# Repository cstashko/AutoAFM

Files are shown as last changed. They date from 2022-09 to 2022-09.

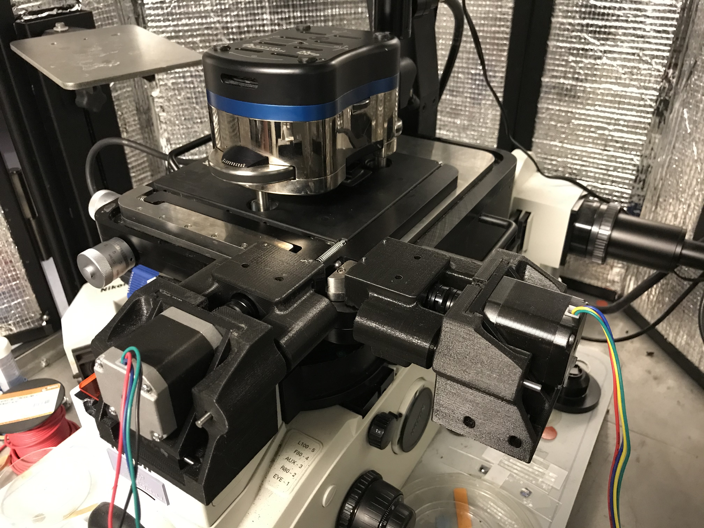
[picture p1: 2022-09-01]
AFM_pics/IMG-1473.jpg

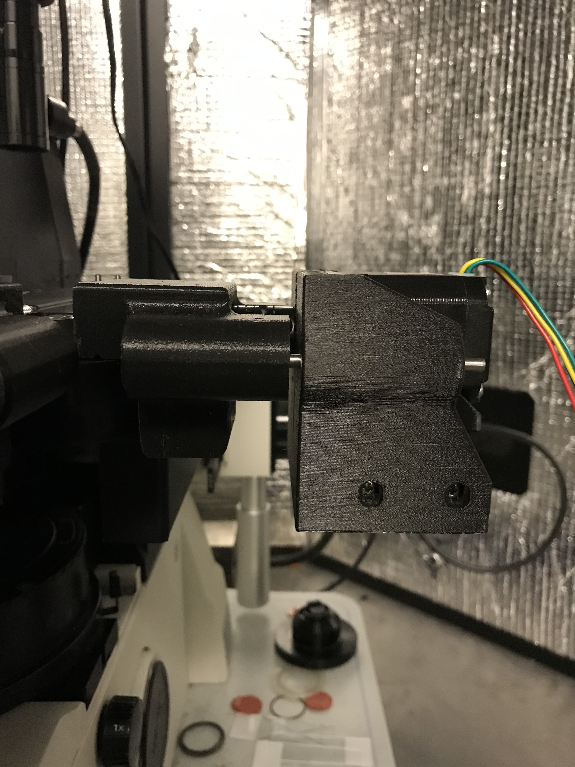
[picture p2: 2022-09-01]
AFM_pics/IMG-1471.jpg

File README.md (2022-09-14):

AutoAFM components, bill of materials, assembled view, and pictures

See STIFMap methods section for in-depth explanation of AutoAFM principles

Contact Connor Stashko (cstashko@berkeley.edu) for questions

AutoAFM Pipeline:  

    1. Thaw slide on hand and wash away OCT in PBS for 5 min  
    2. Probe PA gels of known stiffness as a baseline  
    3. Load tissue sample with approx. 250 uL of PBS + propidium iodide + CNA35   
    4. Open ‘STIFMap_Jupyter_script.ipynb’ in Jupyter and run it all  
    5. Open MicroManager  
        a. Load macros from 'STIFMap_micromanager_macros.txt'  
        b. Manually center AFM stage (in x and y axes)   
        c. Run ‘main’ in micromanager  
            i. Initializes the folders, but don’t do anything else in micromanager yet  
    6. Asylum things: Hook up motors, load ‘STIFMap_IGOR_Asylum_macros.txt’  
        a. Power motors with 12 V  
        b. 'Compile', 'connect', 'initialize', 'initialize'  
        c. Setup WatchFolder (‘WatchFolderPanel()’)  
            i. ‘In’ and ‘out’ in ‘AFM_expt_temp’  
        d. Change save directory to ‘out’ and uncheck ‘save to mem’  
        e. Change trigger to 1.8 nN  
        f. Set the force dist to ‘inf’ and ensure the velocity is 2 um/s  
    7. Move to the region of interest on the slide  
        a. Line up the stage with the optimal position  
        b. Follow the onscreen windows on MicroManager for ‘main’    
    8. Close door to AFM  
    9. At the end, check the position of the tip under BF to ensure it hasn’t changed much  
    10. Probe PA gels again to ensure tip elasticity did not drift during sample probing  
  
Known Issues:  
    • ImageJ won’t move folders/directories if they’re open in file viewer  
    • WatchFolderPanel can’t assign directories that don’t exist, so ‘main’ has to be run before setting input/output dirs  
    • Need a way to quit more elegantly if forcepoints don't trigger in Asylum

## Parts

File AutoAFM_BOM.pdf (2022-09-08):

ITEM NO. | DESCRIPTION | PROCESS | SUPPLIER | MATERIAL | PART NUMBER | QTY. | Package Qty | Unit Price ($) | Order Qty
1 | Microscope Stage_base | AFM Stage Base | INCLUDED | | | 1
2 | Microscope Stage_X | AFM Stage X Translation | INCLUDED | | | 1
3 | Microscope Stage_Y | AFM Stage Y Transation | INCLUDED | | | 1
4 | | AFM X Knob | INCLUDED | | | 1
5 | | AFM Y Knob | INCLUDED | | | 1
6 | | | PURCHASED | MCMASTER | 91290A190 | 4 | 10 | 7.11 | 1 | 7.11
7 | clamp_nut_90576A103 | | PURCHASED | MCMASTER | 90576A103 | 4 | 100 | 4.27 | 1 | 4.27
8 | | | PURCHASED | MCMASTER | 93475A230 | 4 | 100 | 1.86 | 1 | 1.86
9 | X_frame_main | Stage Frame_x | 3D PRINTED | | | 1
10 | NEMA 17 | Motor | INCLUDED | | NEMA 17 | 2
11 | motor_faceplate | Motor Bracket | 3D PRINTED | | | 2
12 | slider | Motor Frame | 3D PRINTED | | | 2
13 | wedge_1 | Bracket Adjuster_front | 3D PRINTED | | | 2
14 | wedge_2 | Bracket Adjuster_back | 3D PRINTED | | | 2
15 | | | PURCHASED | MCMASTER | 9044K113 | 4 | 3 | 5.26 | 2 | 10.52
16 | | Tensioning Pin | PURCHASED | MCMASTER | 91595A140 | 4 | 25 | 9.91 | 1 | 9.91
17 | | Bracket Adjusting Screws | PURCHASED | MCMASTER | 92000A077 | 4 | 50 | 9.94 | 1 | 9.94
18 | wedge_nut_90591A250 | | PURCHASED | MCMASTER | 90591A250 | 4 | 100 | 2.33 | 1 | 2.33
19 | | | PURCHASED | MCMASTER | 97310A111 | 4 | 100 | 2.86 | 1 | 2.86
20 | slider_pin_91585A389 | Alignment Rod | PURCHASED | MCMASTER | 91585A389 | 4 | 1 | 4.14 | 4 | 16.56
21 | motor_screw_91290A111 | Screws Motor into Motor Bracket | PURCHASED | MCMASTER | 91290A111 | 4 | 100 | 8.71 | 1 | 8.71
22 | X_frame_clamp | | 3D PRINTED | | | 1
23 | knob_cap | Knob Adapter | 3D PRINTED | | | 2
24 | knob_screw_90044A247 | Adapter Screw | PURCHASED | MCMASTER | 90044A247 | 2 | 5 | 7.44 | 1 | 7.44
25 | 5mm_hub_9889T106 | Motor Coupling | PURCHASED | MCMASTER | 9889T106 | 2 | 1 | 16.08 | 2 | 32.16
26 | 8mm_Hub_9889T109 | Motor Coupling | PURCHASED | MCMASTER | 9889T109 | 2 | 1 | 16.08 | 2 | 32.16
27 | Acetal_disk_59985K620 | Motor Coupling | PURCHASED | MCMASTER | 59985K62 | 2 | 1 | 3.22 | 2 | 6.44
28 | rubber pad_X | | INCLUDED | | | 1
29 | Yframe_main | Stage Frame_y | 3D PRINTED | | | 1
30 | Yframe_clamp | | 3D PRINTED | | | 1
31 | rubber pad_Y | | INCLUDED | | | 1
32 | rollers_1 | | PURCHASED | MCMASTER | 3668K22 | 2 | 1 | 18.63 | 2 | 37.26
33 | rollers_2 | | PURCHASED | MCMASTER | 3659K11 | 2 | 1 | 36.88 | 2 | 73.76
TOTAL | 263.29

SW-File Name(File
Name)

Extended Price
($)

Microscope
Stage_X_knob
Microscope
Stage_Y_knob
clamp_screw_91290A19
0

Screws frame_main into
frame_clamp
Screws frame_main into
frame_clamp
clamp_washer_93475A2
30

Screws frame_main into
frame_clamp

wedge_spring_5108N27
1

Springs holding Motor Bracket with Motor Frame
wedge_pin_m3x36_9159
5A140 wedge_screw_92000A0
77 | Used with Bracket Adjusting
| Screws
wedge_washer_97310A 111_ | Used with Bracket Adjusting Screws

Clamps Stage Frame_x onto
AFM Stage

Between X_frame_main and
X_frame_clamp

Clamps Stage Frame_y onto
AFM Stage
Between Y_frame_main and
Y_frame_clamp
Screw into Y_frame_main from above
Screw into Y_frame_main from below

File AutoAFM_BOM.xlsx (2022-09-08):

ITEM NO. | SW-File Name(File Name) | DESCRIPTION | PROCESS | SUPPLIER | MATERIAL | PART NUMBER | QTY. | Package Qty | Unit Price ($) | Order Qty | Extended Price ($)
1 | Microscope Stage_base | AFM Stage Base | INCLUDED |  |  |  | 1
2 | Microscope Stage_X | AFM Stage X Translation | INCLUDED |  |  |  | 1
3 | Microscope Stage_Y | AFM Stage Y Transation | INCLUDED |  |  |  | 1
4 | Microscope Stage_X_knob | AFM X Knob | INCLUDED |  |  |  | 1
5 | Microscope Stage_Y_knob | AFM Y Knob | INCLUDED |  |  |  | 1
6 | clamp_screw_91290A19 0 | Screws frame_main into frame_clamp | PURCHASED | MCMASTER |  | 91290A190 | 4 | 10 | 7.11 | 1 | 7.11
7 | clamp_nut_90576A103 | Screws frame_main into frame_clamp | PURCHASED | MCMASTER |  | 90576A103 | 4 | 100 | 4.27 | 1 | 4.27
8 | clamp_washer_93475A2 30 | Screws frame_main into frame_clamp | PURCHASED | MCMASTER |  | 93475A230 | 4 | 100 | 1.86 | 1 | 1.86
9 | X_frame_main | Stage Frame_x | 3D PRINTED |  |  |  | 1
10 | NEMA 17 | Motor | INCLUDED |  |  | NEMA 17 | 2
11 | motor_faceplate | Motor Bracket | 3D PRINTED |  |  |  | 2
12 | slider | Motor Frame | 3D PRINTED |  |  |  | 2
13 | wedge_1 | Bracket Adjuster_front | 3D PRINTED |  |  |  | 2
14 | wedge_2 | Bracket Adjuster_back | 3D PRINTED |  |  |  | 2
15 | wedge_spring_5108N27 1 | Springs holding Motor Bracket with Motor Frame | PURCHASED | MCMASTER |  | 9044K113 | 4 | 3 | 5.26 | 2 | 10.52
16 | wedge_pin_m3x36_9159 5A140 | Tensioning Pin | PURCHASED | MCMASTER |  | 91595A140 | 4 | 25 | 9.91 | 1 | 9.91
17 | wedge_screw_92000A0 77 | Bracket Adjusting Screws | PURCHASED | MCMASTER |  | 92000A077 | 4 | 50 | 9.94 | 1 | 9.94
18 | wedge_nut_90591A250 | Used with Bracket Adjusting Screws | PURCHASED | MCMASTER |  | 90591A250 | 4 | 100 | 2.33 | 1 | 2.33
19 | wedge_washer_97310A 111_ | Used with Bracket Adjusting Screws | PURCHASED | MCMASTER |  | 97310A111 | 4 | 100 | 2.86 | 1 | 2.86
20 | slider_pin_91585A389 | Alignment Rod | PURCHASED | MCMASTER |  | 91585A389 | 4 | 1 | 4.14 | 4 | 16.56
21 | motor_screw_91290A111 | Screws Motor into Motor Bracket | PURCHASED | MCMASTER |  | 91290A111 | 4 | 100 | 8.71 | 1 | 8.71
22 | X_frame_clamp | Clamps Stage Frame_x onto AFM Stage | 3D PRINTED |  |  |  | 1
23 | knob_cap | Knob Adapter | 3D PRINTED |  |  |  | 2
24 | knob_screw_90044A247 | Adapter Screw | PURCHASED | MCMASTER |  | 90044A247 | 2 | 5 | 7.44 | 1 | 7.44
25 | 5mm_hub_9889T106 | Motor Coupling | PURCHASED | MCMASTER |  | 9889T106 | 2 | 1 | 16.08 | 2 | 32.16
26 | 8mm_Hub_9889T109 | Motor Coupling | PURCHASED | MCMASTER |  | 9889T109 | 2 | 1 | 16.08 | 2 | 32.16
27 | Acetal_disk_59985K620 | Motor Coupling | PURCHASED | MCMASTER |  | 59985K62 | 2 | 1 | 3.22 | 2 | 6.44
28 | rubber pad_X | Between X_frame_main and X_frame_clamp | INCLUDED |  |  |  | 1
29 | Yframe_main | Stage Frame_y | 3D PRINTED |  |  |  | 1
30 | Yframe_clamp | Clamps Stage Frame_y onto AFM Stage | 3D PRINTED |  |  |  | 1
31 | rubber pad_Y | Between Y_frame_main and Y_frame_clamp | INCLUDED |  |  |  | 1
32 | rollers_1 | Screw into Y_frame_main from above | PURCHASED | MCMASTER |  | 3668K22 | 2 | 1 | 18.63 | 2 | 37.26
33 | rollers_2 | Screw into Y_frame_main from below | PURCHASED | MCMASTER |  | 3659K11 | 2 | 1 | 36.88 | 2 | 73.76
 |  |  |  |  |  |  |  |  |  | TOTAL | 263.29

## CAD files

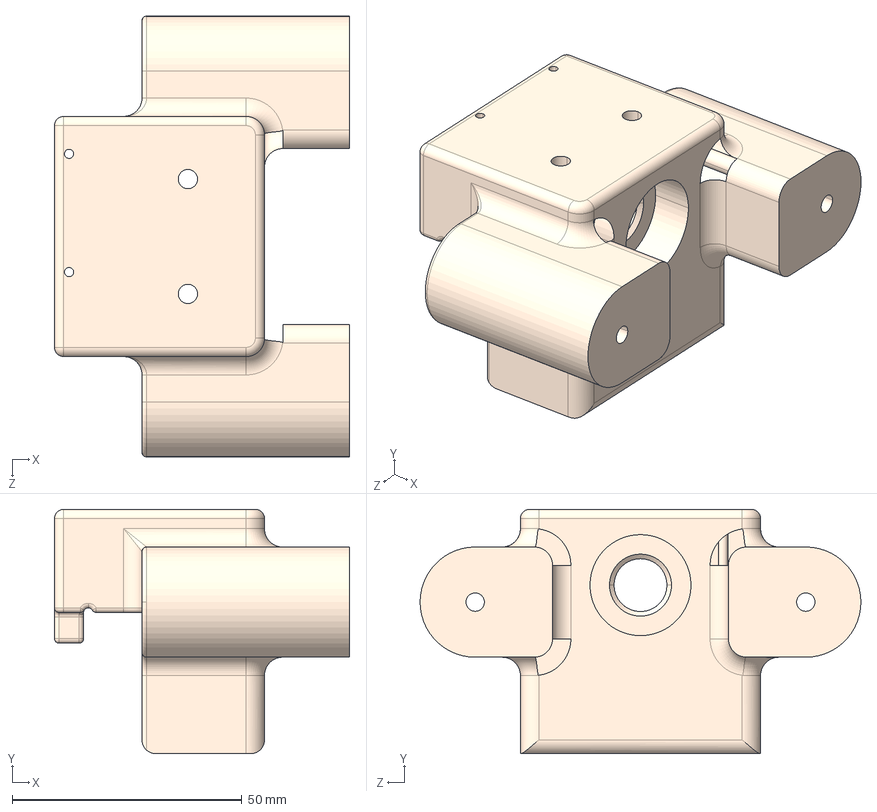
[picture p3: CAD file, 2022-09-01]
STEP/X_frame_main.STEP
64.2 x 53.2 x 96.0 mm

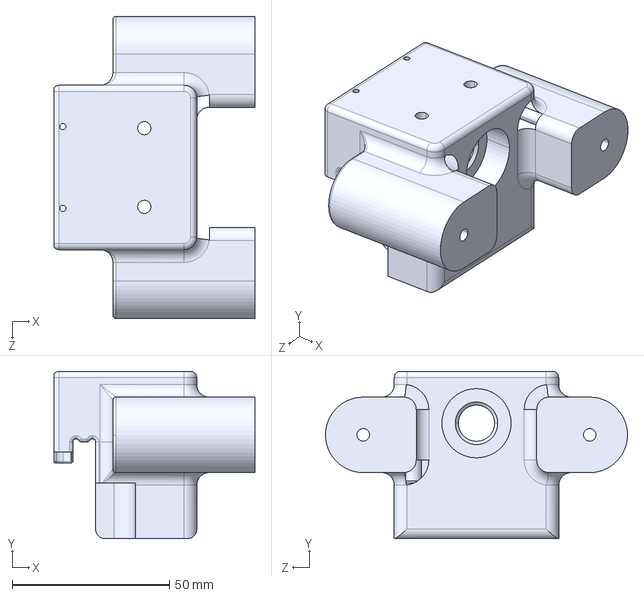
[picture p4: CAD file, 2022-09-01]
STEP/Yframe_main.STEP
63.9 x 53.2 x 96.0 mm

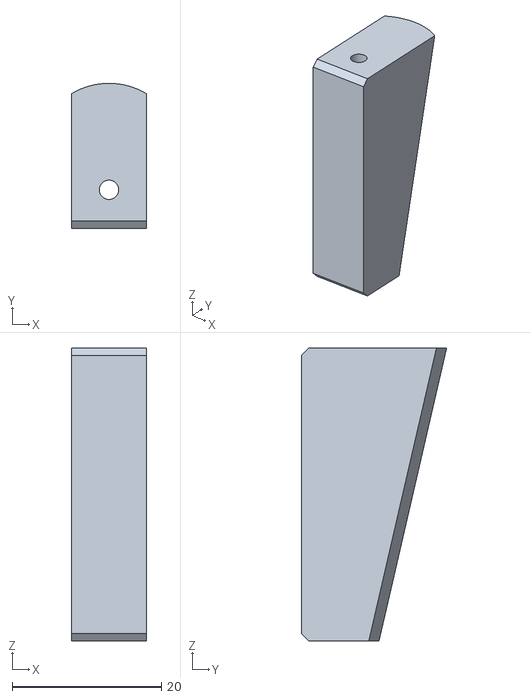
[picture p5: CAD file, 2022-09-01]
STL/wedge_1.STL
10.0 x 19.5 x 39.3

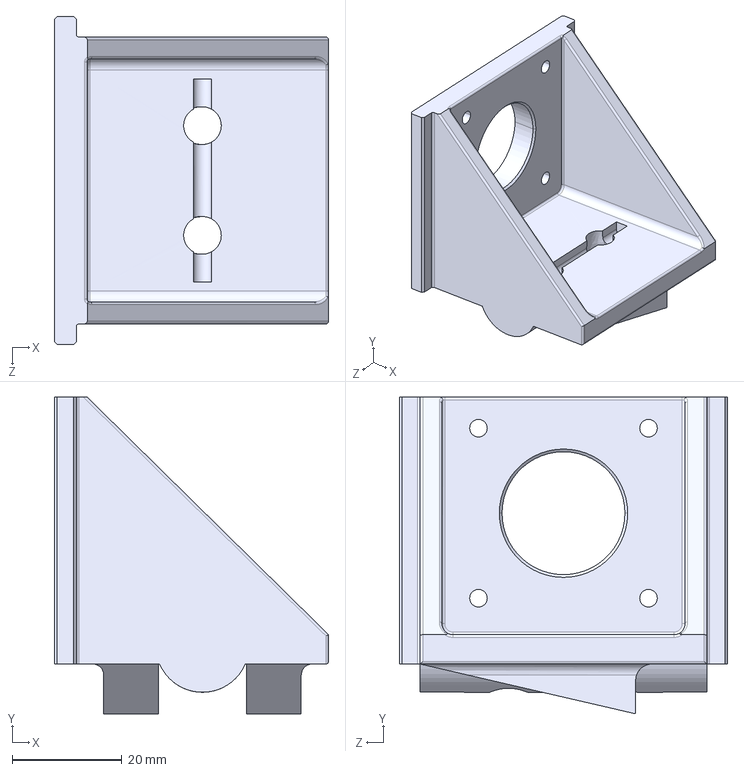
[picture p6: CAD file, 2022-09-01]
STEP/motor_faceplate.STEP
50.0 x 57.7 x 59.8 mm

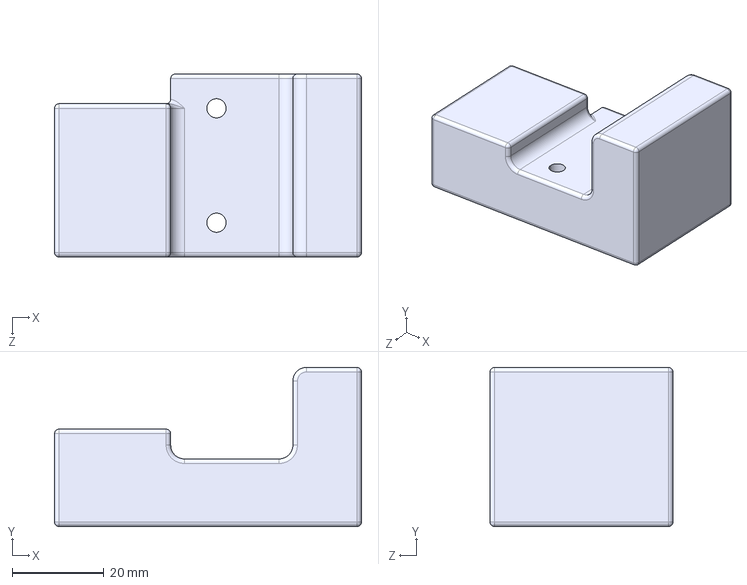
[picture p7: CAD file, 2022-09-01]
STEP/X_frame_clamp.STEP
67.1 x 34.8 x 40.0 mm

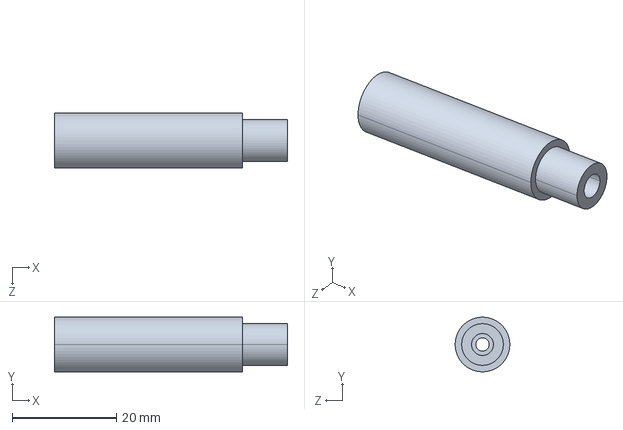
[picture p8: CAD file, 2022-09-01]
STEP/knob_cap.STEP
44.7 x 10.5 x 10.5 mm

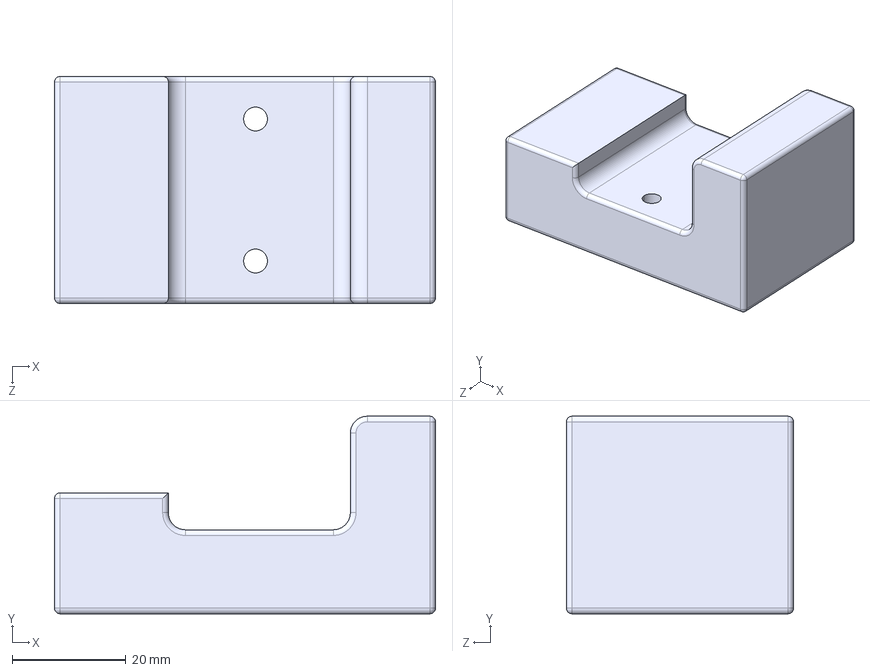
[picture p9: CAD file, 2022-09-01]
STEP/Yframe_clamp.STEP
67.1 x 34.8 x 40.0 mm

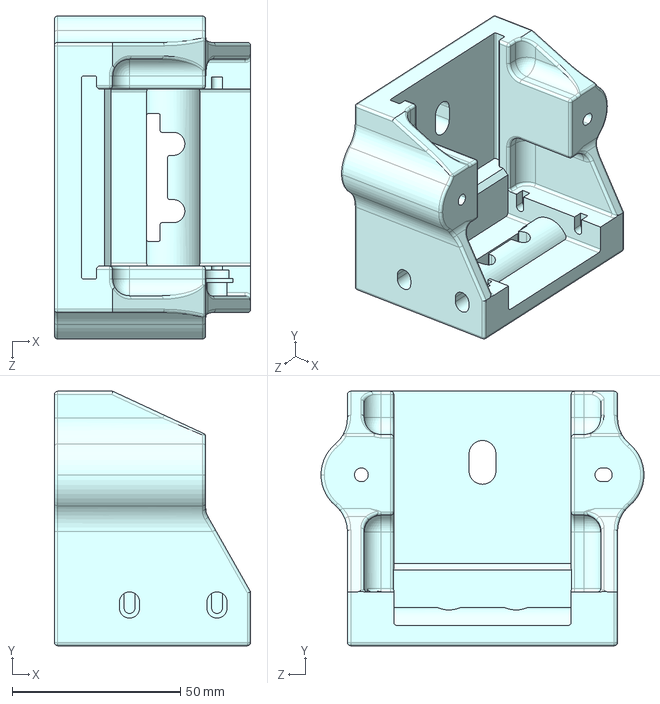
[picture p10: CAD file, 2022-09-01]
STEP/slider.STEP
58.3 x 75.7 x 96.0 mm

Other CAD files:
STL/wedge_2.STL
STL/X_frame_clamp.STL
STL/X_frame_main.STL
STL/Yframe_clamp.STL
STL/Yframe_main.STL
STL/knob_cap.STL
STL/motor_faceplate.STL
STL/slider.STL
